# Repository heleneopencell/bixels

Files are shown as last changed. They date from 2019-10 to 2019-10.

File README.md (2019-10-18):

# bixels
 
This document will show you how to visualize fluorescent proteins with a simple DIY transilluminator / plate reader. Fluorescent proteins are widely used in biology as a research aid. In standard bio-labs you would use a transilluminator or platereader to visualize them which are wildly expensive. We will make a simple and very low-cost version of this which can be also used as a 8x8 biodisplay or as a STEAM education kit to get kids excited about biotechnology.  

[More info](https://www.bixels.io/tutorials)

### 1)[Electronic parts](https://github.com/heleneopencell/bixels#1electronic-parts)
### 2)[Cardboard box](https://github.com/heleneopencell/bixels#2cardboard-box-1)
### 3)[Assembly](https://github.com/heleneopencell/bixels#3assembly-1)
### 4)[Software](https://github.com/heleneopencell/bixels#4software-1)
### 5)[GFP - Green fluorescent proteins](https://github.com/heleneopencell/bixels#5gfp---green-fluorescent-proteins-1)
### 6)[Run an experiment](https://github.com/heleneopencell/bixels#6run-an-experiment-1)
### 7)[Timelapse with webcam](https://github.com/heleneopencell/bixels#7timelapse-with-webcam-1)
### 8)[Design Ideas](https://github.com/heleneopencell/bixels#8design-ideas-1)
### 9)[Material list](https://github.com/heleneopencell/bixels#overview-materials)
  
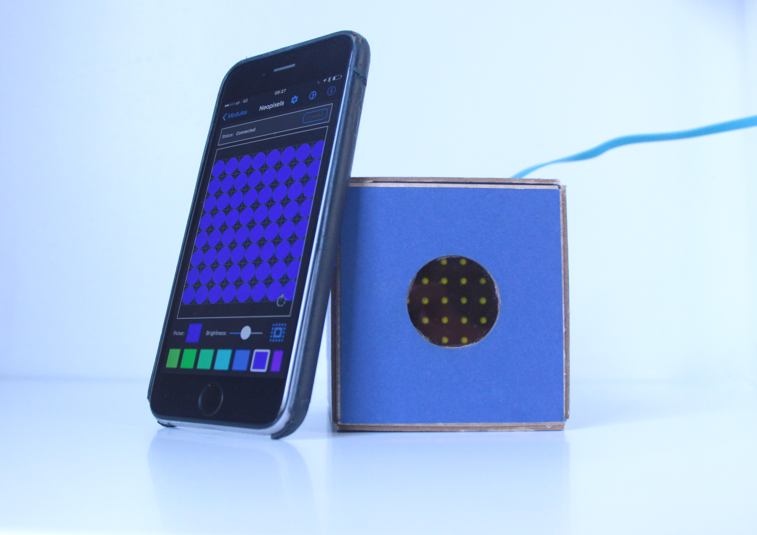
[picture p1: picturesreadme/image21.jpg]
final project
  

##### Overview
A fluorescent protein is a type of fluorescent chemical compound (fluorophore) that can re-emit light upon light excitation. If one colour of light lands on a fluorescent protein, the protein will glow with a different colour.

The story of the extraction, isolation and study of **green fluorescent protein (GFP)** is fascinating. It is also a hugely significant scientific discovery for which the 2008 Nobel Prize in Chemistry was awarded.

In this tutorial we will show you how to visualize fluorescent proteinswe. We will build a cardboard box to block out any unwanted light and use a set of optical filters. The filters allow the correct light to reach the fluorescent proteins from the LEDs and for the correct light to reach your eye from the fluorescent proteins. The diffuser simply diffuses the light evenly which is not necessary but useful if you want to use Bixels for something else than PCR tubes, for example electrophoresis gels. 

The RGB LED matrix we are using is capable of generating the required light to stimulate fluorescence in many types of fluorescent proteins.  
The filters described in this tutorial are only suitable for GFP but you can exchange them.[You can learn more here](https://www.biotek.com/assets/tech_resources/Filter%20Combinations.pdf) which filters to use for which fluorescent protein.  

The software and app we will use will allow you to control each single led and it's individual light color from your phone.  

Proteins can take up to a few hours to get expressed. We therefore added a section how to add a webcam to Bixels which takes every few minutes a picture which will create a timelapse streamed to the web. 

_____________________

### 1)Electronic parts
We will be using off-the-shelf electronics from adafruit for this project. Adafruit is super user friendly, fantastic for quick DIY projects and has a huge community to reach out for help and inspiration.
We will be using their [Adafruit Feather 32u4](https://www.adafruit.com/product/2829) board which is bluetooth enabled to control a [8x8 Neopixel LED matrix](https://www.adafruit.com/product/1487) with our phone. To power bixels we will add a [micro USB breakout](https://www.adafruit.com/product/1833). This enables you to power bixels with a power bank, your laptop or with a wall plug.

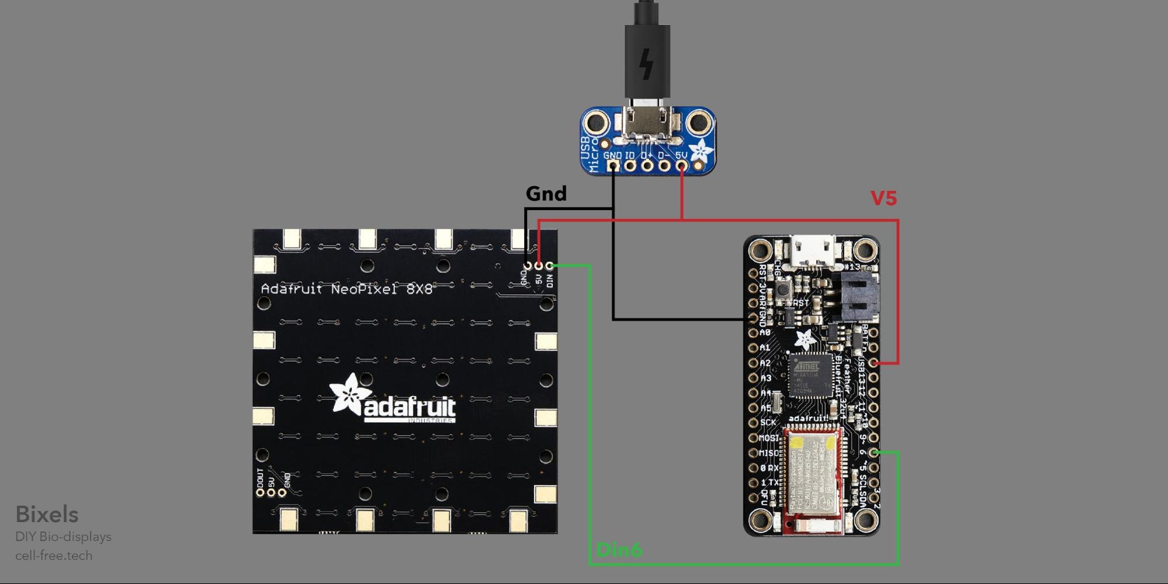
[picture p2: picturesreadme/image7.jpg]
electronic circuit


To start with we have to solder the stacking headers on the Adafruit Feather and Neopixel Matrix. I recommend using the headers rather than soldering the cables directly on the board. The headers will allows you to be much for flexible and enable you to expand your project at a later stage with useful sensors such as humdity and temperature. For the ones that are new to soldering, check out this usefull [guide to excellent soldering](https://learn.adafruit.com/adafruit-guide-excellent-soldering).

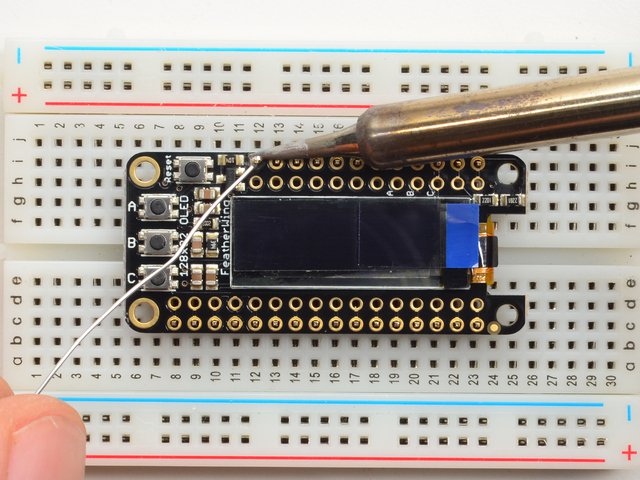
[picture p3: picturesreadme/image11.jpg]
soldering bluefruit


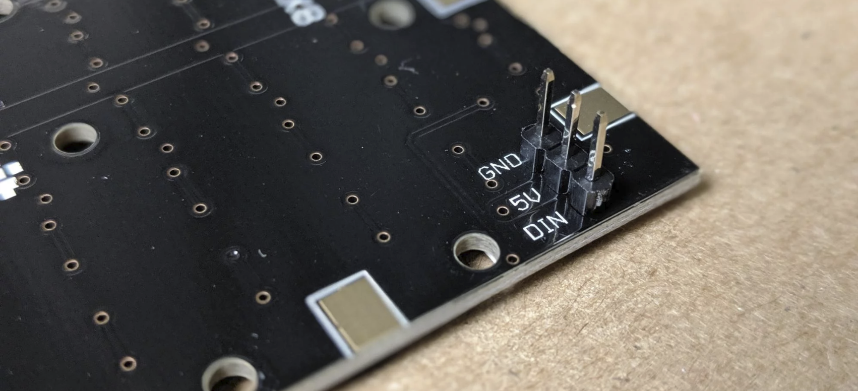
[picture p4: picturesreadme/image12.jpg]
soldering neopixel
  

To power bixels we will add a micro usb port. Take two black or brown "female to female" jumper wires and cut one end off. Connect the wire end with each other and solder it on the GND pin on the USB Micro B-Breakout board. Now take two red "female to female" jumper wire wires and cut one end off. Connect the wire end with each other and solder it on the 5V pin on the USB Micro B-Breakout board. We will use one black and one red cable to power the LEDs and one black and one red one to power the board itself.  

Note: You can also make your own wires with femaler headers but I do it the lazy way...
  
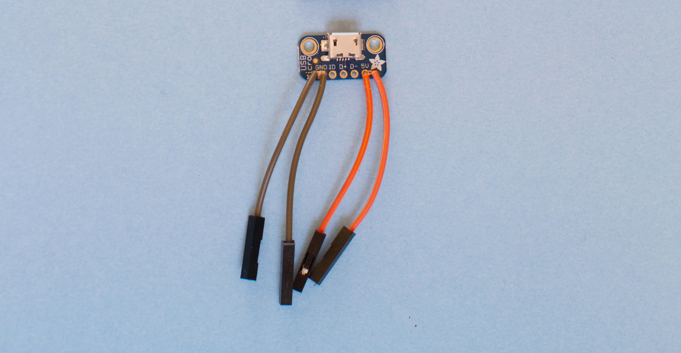
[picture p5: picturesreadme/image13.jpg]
soldering microusb


### 2)Cardboard box
Let's get started with the cover for bixels which is a simple cardboard box. I have chosen cardboard because it allows you to quickly iterate and customize the design without the need of any equipment such as a 3D printer. 

You can either lasercut your parts or print the PDF on a A3 sheet and cut it out by hand. Use a non see-through cardboard! Test it out beforehand and hold it against the light. No light should be able to get through. I use [Mountboard from Daler Rowney](https://www.amazon.co.uk/Daler-Rowney-Black-Graduate-Mountboard/dp/B00GKCF0VG/ref=sr_1_4?keywords=mount+board+black&qid=1571151582&sr=8-4) because it allows you to make neat hinges. You can also add a layer of black thin cardboard on each side if your cardboard let's any light through, use sprayglue for laminating it on top.
 
###### For the lasercut
[Download](https://github.com/heleneopencell/bixels/tree/master/lasercut) the file here. The yellow lines are for engraving the cardboard to easier fold it. The red lines are cuts. We suggest to test your two settings in a small corner beforehand.  
 
###### For cutting it by hand
[Download](https://github.com/heleneopencell/bixels/tree/master/printfiles) the files here. Print it on an A3 paper and mount it on a thicker cardboard. You don’t want anything moving. I suggest to use (removable) spray-mount for it. For the PCR matrix and it is best to use a lasercutter but it is possible to cut it by hand - a holepuncher is useful. (Just a bit fiddly)  

Note: We have made two designs for the filterbox:  

**Smaller round cut-out:** The benefit here is that less natural light gets in the box which improves the performance. This is particular useful if are planning to use it with a camera. Which I will explain in more detail in [chapter 4](chapter 4).  
**Larger cut-out:** This works better if you want to turn it into a bio-display. You can do fun things such as building your own bio-gameboy with it. Downside is that it works best in the dark because it lets more natural light in. You can also improve this by using 2 blue flights on top of each other.
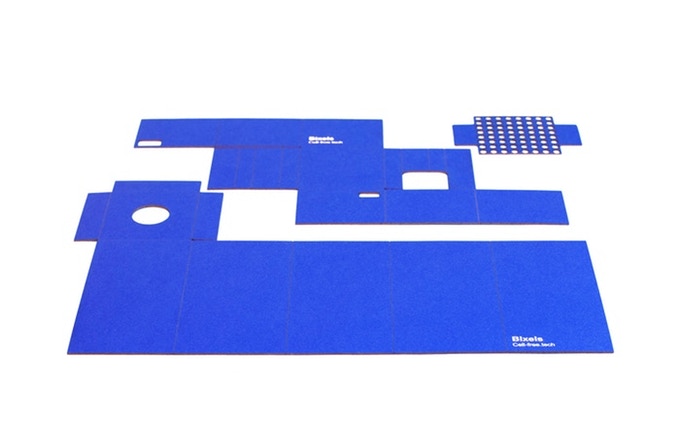
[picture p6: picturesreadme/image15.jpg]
lasercut box
  
  
### 3)Assembly
 
###### Folding the boxes
Bixels is made of 3 parts. The main box for the electronics, the filterbox to turn it into a transilluminator and our PCR matrix to hold your PCR strips in place.

First we have to mount the USB breakout board on the main box with the two M2 screws and nuts. Now let's **fold the main box** for the electronics: The inner box will be used as a platform for your led-display.  
  
fold mainbox (https://vimeo.com/259026890)

Now let’s **fold the filter box**: Glue the orange filter from on top of the cut-out. We have made two designs for this:  

**Smaller round cut-out:** The benefit here is that less natural light gets in the box which improves the performance. This is particular useful if are planning to use it with a camera. Which I will explain in more detail in [chapter 4](chapter 4).  

**Larger cut-out:** This works better if you want to turn it into a bio-display. You can do fun things such as building your own bio-gameboy with it. Downside is that it works best in the dark because it lets more natural light in. You can also improve this by using 2 blue flights on top of each other.  

fold filterbox (https://vimeo.com/259029617)

Let's **fold the PCR matrix:**  
The PCR matrix is designed to fit with PCR strips which will place each PCR tube right on top of an LED. Fill the matrix when you are ready to make your experiment to ensure they are sterile.
It is a simple matrix which can be connected without the use of any glue.  

pcr matrix (https://vimeo.com/259033478)  

Next let's connect all electronics. Connect one of the **red wires** from the micro usb breakout board to the **5V pin** on the Neopixel matrix and one red wire to the **USB pin** on Bluefruit feather board.
Now connect one of the **black wires** from the micro usb breakout board to the **GND pin** on the Neopixel matrix and one black wire to the **GND pin** on Bluefruit feather board. Next grab one of the female/female **jumper wires** and connect the **DIN pin** on the Neopixel matrix with **Pin6** on the Bluefruit feather board. Hide carefully the board in the little compartment and place the LED matrix on top. Connect the usb cable and we are ready to go.
  
assembly (https://vimeo.com/259130358)  

### 4)Software  

###### Arduino set-up for Adafruit Feather 32u4 
If you haven’t done it already, download the newest [Arduino IDE version](https://www.arduino.cc/en/main/software). Next we have to set up our Bluefruit Feather Board for Arduino as described [here](https://learn.adafruit.com/adafruit-feather-32u4-bluefruit-le/setup) and install the board with the Board Manager and install the adafruit driver as described [here](https://learn.adafruit.com/adafruit-feather-32u4-bluefruit-le/using-with-arduino-ide).  

###### Uploading Arduino sketch 
Before uploading our sketch you need to install the BLE library as described [here](https://learn.adafruit.com/adafruit-feather-32u4-bluefruit-le/installing-ble-library). 
Now download the [bixel.zip](/bixel.zip), extract or unpack it and open the file bixel.ino which is inside the folder.

It’s time to upload your code onto your device. Connect the USB from your bixel to your computer and choose the correct port inside your Arduino window. Now click upload and wait till it got successfully uploaded. It should look something like this.

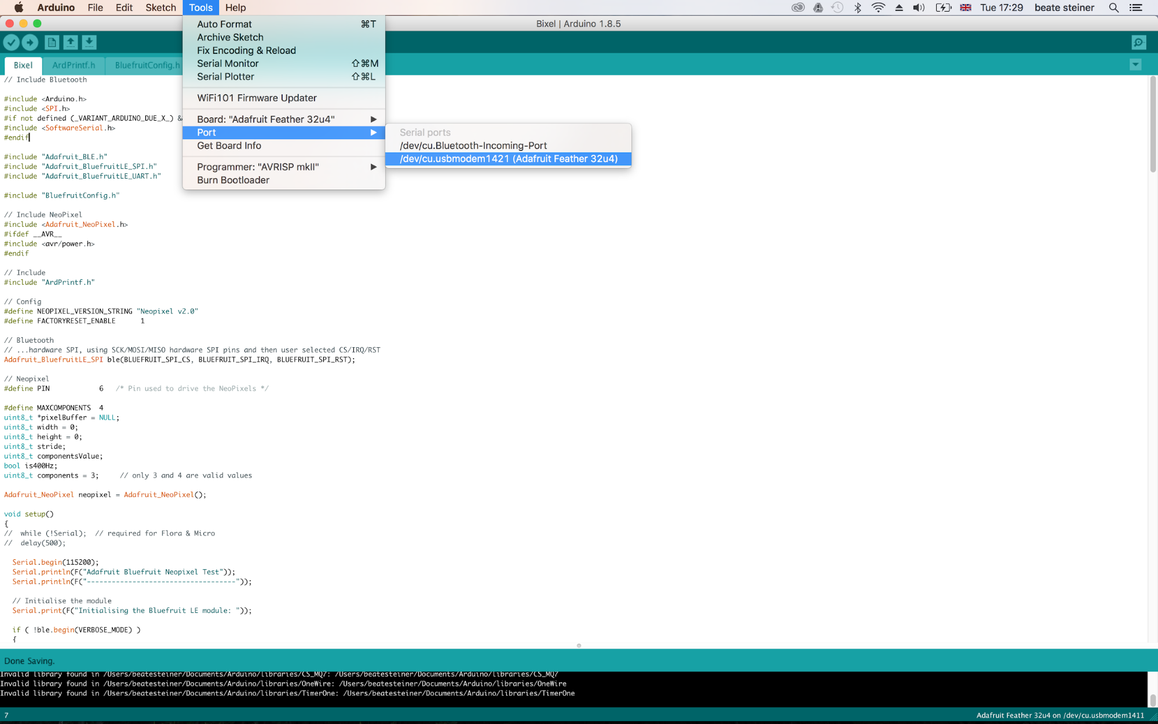
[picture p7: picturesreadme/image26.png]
choose port
  
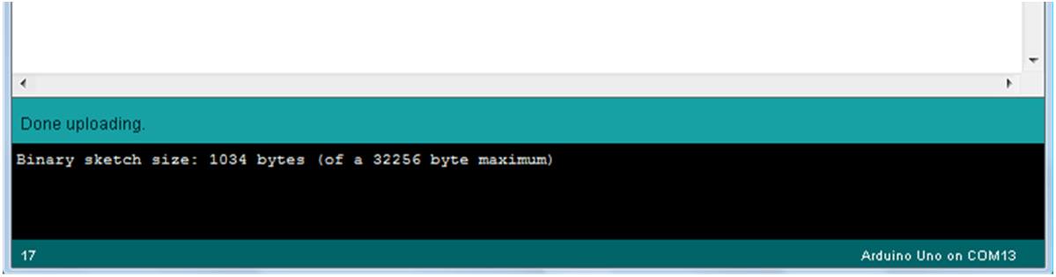
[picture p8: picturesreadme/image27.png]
upload
  
  
###### App to control the LED's
Now let’s get started with controlling the LEDs. First download the Adafruit Bluefruit LE Connect App on your phone. The app is available for [iOS](https://apps.apple.com/gb/app/adafruit-bluefruit-le-connect/id830125974) and [Android](https://play.google.com/store/apps/details?id=com.adafruit.bluefruit.le.connect&hl=en_GB).
 
Open the app and connect to your device Adafruit Bluefruit LE.
Choose the NeoPixel icon in the bottom line and press OK when it gives you a notice.
Next we have to choose the correct matrix layout. Click the settings button at the top, next to the word ‘NeoPixel’ and choose ‘8x8’.
Press ‘Connect’ and your LED’s should turn on. Now you are ready to control your individual LEDs. 

assembly (https://vimeo.com/259016118)  

### 5)GFP - Green fluorescent proteins
We need a fluorescent protein to be able to test if our transilluminator is working! So how do we make them?

In most cases we talk and share how to programme with 0's and 1's on this platform but here we would like to share how to programme with DNA, with C G T and A's.  
At the cellular level organisms are complex. A key process is the creation of proteins based on the specific instructions contained in the base pairings of deoxyribonucleic acid (DNA). Base-pairs are composed of either cytosine (C) and guanine (G) or tyrosine (T) and adenine (A). These base pair instructions can be long, the genome of a human is ~ 3 billion base pairs (3gbp), the genome of wheat is even longer at 10 gbp. The length of DNA which encodes green fluorescent protein (a single protein, and the topic of this tutorial) is about 700 bp.  

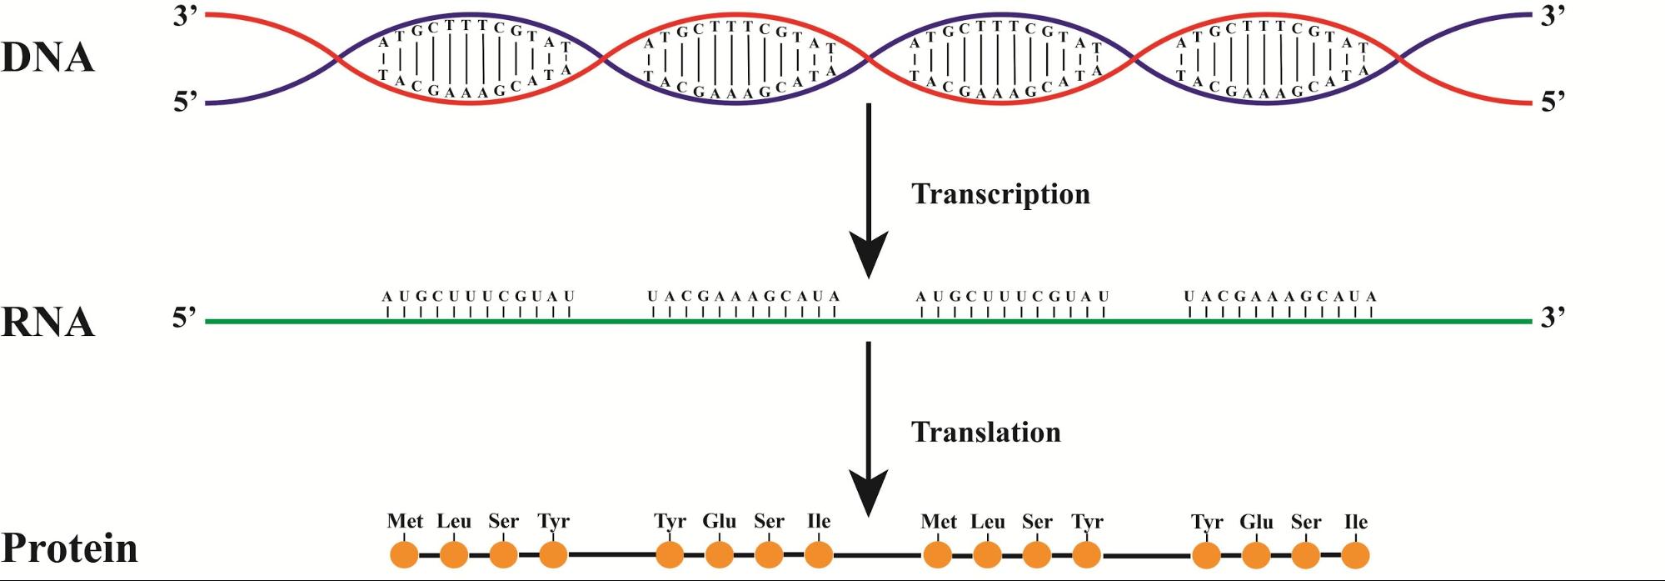
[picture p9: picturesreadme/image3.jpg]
  

A selection of DNA is transcribed when a type of protein called RNA polymerase attaches to a circuit element called a promoter (initiator of transcription), this creates a piece of RNA of length determined by the location of a terminator (stops transcription). This piece of RNA contains a ribosome-binding site to which an organelle called a ribosome adheres and begins the process of translation, where amino acid sequences are joined to form proteins. 

A piece of **DNA gives these instructions** through encoding specific operations:
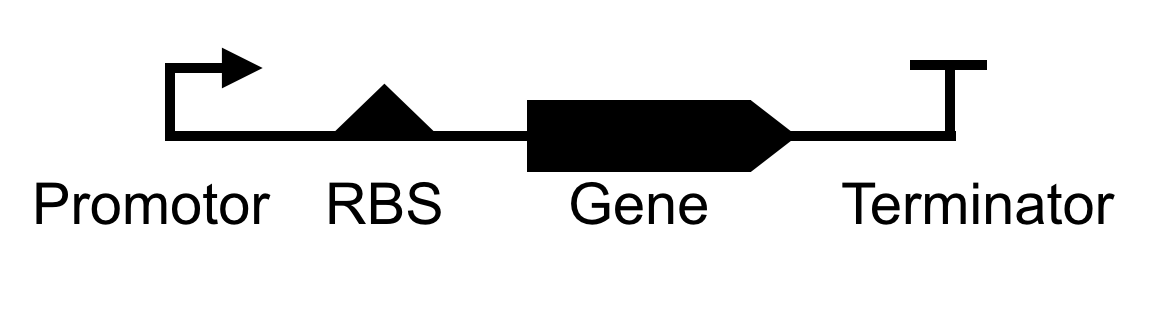
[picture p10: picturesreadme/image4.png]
  

* Promoter -  Facilitates RNA polymerase binding to initiate transcription
* Ribosome-binding site (RBS) - Initiation site for translation
* Gene - The part of the DNA code that is converted to the protein of interest
* Terminator - Halts transcription

###### How to Engineer Biology

Synthetic biology is an interdisciplinary branch of biology and engineering. It establishes the tools and techniques to build artificial biological systems for various applications. Some of the best materials to work with in this field are the simplest and most common - like DNA.

In order to understand DNA you can use a visualiser and a great service to use for this is [Benchling](https://www.benchling.com/). To get even more hands on and do it yourself you can review two sites that have everything you could ever need in terms of DNA parts. The first is Addgene, a non-profit set up with the goal of providing a facility for maintaining and storing DNA parts. They have a [dedicated site about fluorescent proteins](https://www.addgene.org/fluorescent-proteins/).  It is roughly £60 for an individual part. Secondly you could go to the [IGEM registry](http://parts.igem.org/Protein_coding_sequences/Reporters#Fluorescent_proteins) where a whole range of parts or “biobricks” are stored and can be requested (although you may need to be part of an IGEM team).

For Bixels we want to produce green fluorescent proteins, these  will glow with a different colour when one colour of light hits them. A wide range of coloured proteins (fluorophores) can be produced from DNA. This allows you to get creative with your combinations.   
  
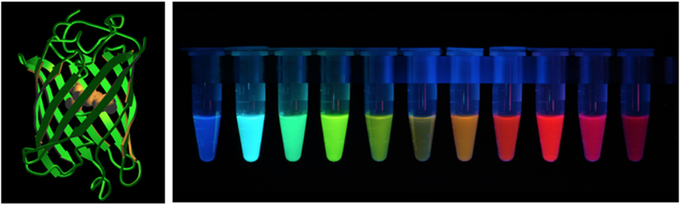
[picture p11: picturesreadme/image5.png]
different colors
  

Note: Bear in mind that different coloured proteins need to get excited with a different colour of light, which means you also have to adapt your filters. [Here](https://www.biotek.com/assets/tech_resources/11596/table1.jpg) a useful document about the different excitation wavelenghts for different proteins.
But first let's find out how to even make proteins. We will outline two ways here:

1) **By bacteria transformation**
This involves inserting a plasma into a chassi, for example E.Coli (bacteria) which will express proteins based on the plasmid incerted.
If you are new to genetic engineering we highly recommend you to get the [Zero to genetic engineering hero book](https://amino.bio/products/learn-genetic-engineering-the-genetic-engineering-hero-book) from Amino Labs. It will make teach you every step needed to make your own transformations. With the book you can get kits that will provide you with all materials needed to make your own fluorescent proteins. I recommend the [RGB kit](https://amino.bio/collections/everything/products/rgb-kit-activate-cells-with-light)!

2) **By using Cell-Free systems**
Which allows you to use and work with outside of the research lab. This involves removing the transcription and translation machinery from a cell. It allows you to make proteins without having to grow or work with live cells. Since Cell-Free expression liberates you from the requirements of a bio-lab you can begin to experiment to make your projects more tangible. You can get your cell-free kit to make your own fluorescent proteins at [minipcr.com](https://www.minipcr.com/product/biobits-central-dogma/).

### 6)[Run an experiment]()
Let's make your proteins shine. 

I love that the colors of the app are similar to different protein you can express. In our case we will excite a green fluorescent protein with blue light.
So let's turn your bixel into a transilluminator. The kit includes 3 filters. An amber filter, blue filter and and a diffuser.
We already mounted our amber filter into our filter box. To turn the main box into a transilluminator, layer the blue filter and diffuser on top of the LED matrix and place your PCR matrix (with GFP in 1 or more tubes) on top. Slide the filter box on top of the main box and turn the LEDs to blue. You can either excite single tubes or excite all in once.  

assembly (https://vimeo.com/236662582)  

If you look now through the orange filter you will only see your fluorescent proteins glow! I love to use either my phone to capture it or for timelapses a simple web-cam. Below a protocol ‘How to build a timelapse with a web-cam’.  

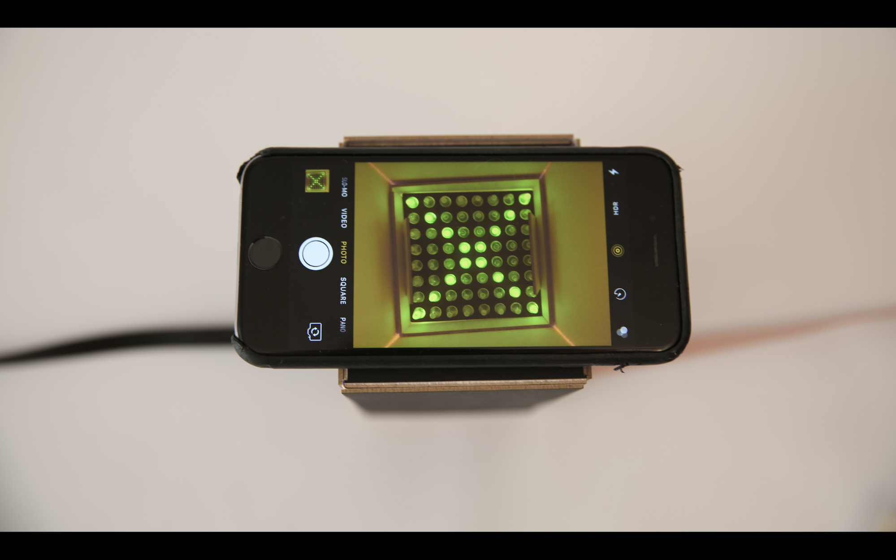
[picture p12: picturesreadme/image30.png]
transilluminator
  

### 7)Timelapse with webcam
I like to use electronics and programming not only to be creative, it allows me to be lazy.
My colleague Tom wrote a tutorial how to make a cheap timelapse and webstream with a Raspberry Pi and a webcam.
The design fits great with the bixels project. [Follow the steps here.](http://designbio.co.uk/blog/raspi-timelapse)

### 8)Design Ideas
Now it's time to get creative. We have used bixels for some fun applications so far:

**As an educational tool to teach biotechnology to non scientists**  
educational tool (https://vimeo.com/212755100)  

**Making a gameboy which has a biopixel display**  
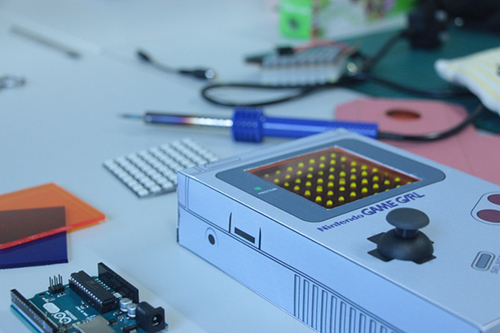
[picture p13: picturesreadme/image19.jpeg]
  

**Playing tetris with fluorescent proteins**  
  

**Test your biology experiment**  
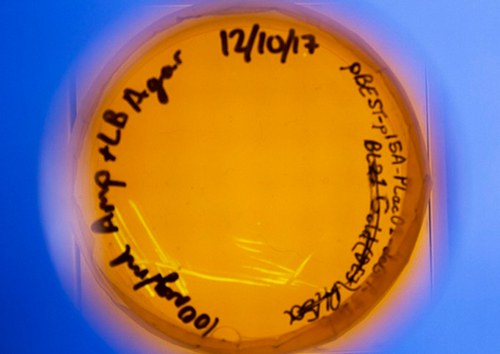
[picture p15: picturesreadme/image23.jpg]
lab
  

If you have any ideas you want to share please drop me a line at helene.steiner@rca.ac.uk

### Overview Materials  

| Electronic Parts  | Supplier EU  | Supplier US  |
|-------------------|--------------|--------------|
| 1x Neopixel Matrix |[RS Components](https://uk.rs-online.com/web/p/led-evaluation-kits/1245498/) | [Adafruit](https://www.adafruit.com/product/1487) |
| 1x Adafruit Feather 32u4 | [RS Component](http://tiny.cc/xpbmez) | [Adafruit](https://www.adafruit.com/product/2829) |
| 1x USB Micro B-Breakout   | [Amazon](http://tiny.cc/k0bmez) | [Adafruit](https://www.adafruit.com/product/1833) |
| 1x Jumper wire female/female | [RS Components](https://uk.rs-online.com/web/p/breadboard-jumper-wire-kits/7916450/) | [Adafruit](https://www.adafruit.com/product/1951)|
| 1x Micro USB Cable | [RS Components](https://uk.rs-online.com/web/p/usb-cables/8762403/) | [Adafruit](https://www.adafruit.com/product/1995)|

_____________________
  
| Filters | Supplier EU | Supplier US  |
|-------------------|--------------|--------------|
| 1x Diffuser Paper 72mm x 72mm |[Amazon](http://tiny.cc/7ecmez) | [Amazon](https://www.adafruit.com/product/1487) |
| 1x Translucent Amber Filter 72mm x 72mm | [Plastic People](https://www.theplasticpeople.co.uk/coloured-acrylic-perspex/) | [Acrylite](https://www.mcmaster.com/85635k461) |
| 1x Translucent Blue Filter 72mm x 72mm | [Plastic People](https://www.theplasticpeople.co.uk/coloured-acrylic-perspex/) | [Acrylite](https://www.mcmaster.com/85635k461) |
_____________________
  
| Cover / Box | Supplier EU  | Supplier US  |
|-------------------|--------------|--------------|
| 1x Cardboard |[Amazon](http://tiny.cc/vwdmez) | [Amazon](http://tiny.cc/xzdmez) |
| 1x Double sided tape| [Amazon](http://tiny.cc/fqdmez) | [Amazon](http://tiny.cc/jtdmez) |
| 1x Superglue | [Amazon](http://tiny.cc/9odmez) | [Amazon](http://tiny.cc/nndmez)|
| 2x M2 Hex Nut | [RS Compnent](https://uk.rs-online.com/web/p/hex-nuts/0560271/) | [Amazon](http://tiny.cc/nndmez)|
| 2x M2 Hex Screw | [RS Compnent](https://uk.rs-online.com/web/p/connector-screws-nuts/1665038/) | [Amazon](http://tiny.cc/nndmez)|

_____________________
  
| Equipment | Supplier EU  | Supplier US  |
|-------------------|--------------|--------------|
| Lasercutter or | local makerlab | local makerlab |
| Cutter | [Amazon](https://www.amazon.co.uk/Silverline-789397-Zinc-Alloy-Snap-Off-Utility/dp/B003TNYHHW/ref=sr_1_5?keywords=cutter&qid=1571219430&sr=8-5) | [Amazon](http://tiny.cc/6gdmez) |
| Mobile phone | Android or | iOS |
_____________________
  
| Software | Supplier EU  | Supplier US  |
|-------------------|--------------|--------------|
| Arduino |[Windows](https://www.arduino.cc/en/guide/windows) | [OS X](https://www.arduino.cc/en/guide/macOSX) |
| Bluefruit LE Connect | [Android](https://play.google.com/store/apps/details?id=com.adafruit.bluefruit.le.connect&hl=en_GB) | [iOS](https://apps.apple.com/gb/app/adafruit-bluefruit-le-connect/id830125974) |
_____________________
  
| Biological Parts | Supplier EU  | Supplier US  |
|-------------------|--------------|--------------|
| Fluorescent Protein Kit (RGB) |[Amino Labs](https://amino.bio/collections/everything/products/rgb-kit-activate-cells-with-light) | [Amino Labs](https://amino.bio/collections/everything/products/rgb-kit-activate-cells-with-light) |
| Mini Lab: BioExplorer™  | [Amino Labs](https://amino.bio/collections/everything/products/bioproduction-lab?variant=40528228676) | [Amino Labs](https://amino.bio/collections/everything/products/bioproduction-lab?variant=40528228676) |
| Cell-Free  | [Mini PCR](https://www.minipcr.com/product/biobits-central-dogma/) | [Mini PCR](https://www.minipcr.com/product/biobits-central-dogma/)|
_____________________
_____________________

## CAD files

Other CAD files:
lasercut/pcrmatrix.dxf

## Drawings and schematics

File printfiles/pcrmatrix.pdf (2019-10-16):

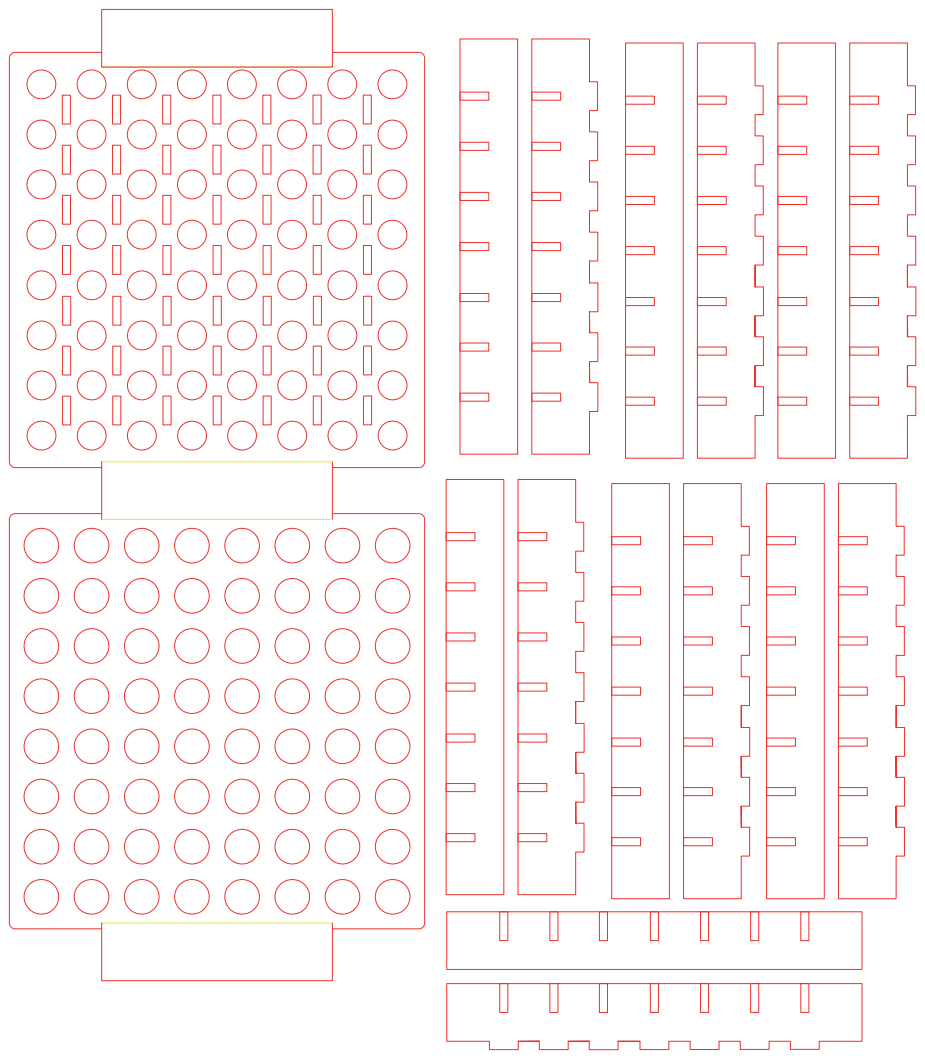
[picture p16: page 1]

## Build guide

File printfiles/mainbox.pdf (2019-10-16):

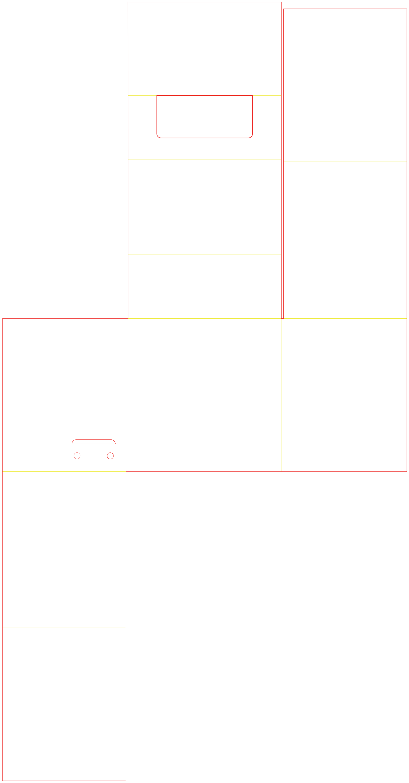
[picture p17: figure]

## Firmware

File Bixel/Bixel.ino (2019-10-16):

// Include Bluetooth

#include <Arduino.h>
#include <SPI.h>
#if not defined (_VARIANT_ARDUINO_DUE_X_) && not defined (_VARIANT_ARDUINO_ZERO_)
#include <SoftwareSerial.h>
#endif

#include "Adafruit_BLE.h"
#include "Adafruit_BluefruitLE_SPI.h"
#include "Adafruit_BluefruitLE_UART.h"

#include "BluefruitConfig.h"

// Include NeoPixel
#include <Adafruit_NeoPixel.h>
#ifdef __AVR__
#include <avr/power.h>
#endif

// Include
#include "ArdPrintf.h"

// Config
#define NEOPIXEL_VERSION_STRING "Neopixel v2.0"
#define FACTORYRESET_ENABLE      1

// Bluetooth
// ...hardware SPI, using SCK/MOSI/MISO hardware SPI pins and then user selected CS/IRQ/RST
Adafruit_BluefruitLE_SPI ble(BLUEFRUIT_SPI_CS, BLUEFRUIT_SPI_IRQ, BLUEFRUIT_SPI_RST);

// Neopixel
#define PIN            6   /* Pin used to drive the NeoPixels */

#define MAXCOMPONENTS  4
uint8_t *pixelBuffer = NULL;
uint8_t width = 0;
uint8_t height = 0;
uint8_t stride;
uint8_t componentsValue;
bool is400Hz;
uint8_t components = 3;     // only 3 and 4 are valid values

Adafruit_NeoPixel neopixel = Adafruit_NeoPixel();

void setup()
{
//  while (!Serial);  // required for Flora & Micro
//  delay(500);

  Serial.begin(115200);
  Serial.println(F("Adafruit Bluefruit Neopixel Test"));
  Serial.println(F("------------------------------------"));

  // Initialise the module
  Serial.print(F("Initialising the Bluefruit LE module: "));

  if ( !ble.begin(VERBOSE_MODE) )
  {
    error(F("Couldn't find Bluefruit, make sure it's in CoMmanD mode & check wiring?"));
  }
  Serial.println( F("OK!") );

  // Factory Reset
  if ( FACTORYRESET_ENABLE )
  {
    /* Perform a factory reset to make sure everything is in a known state */
    Serial.println(F("Performing a factory reset: "));
    if ( ! ble.factoryReset() ) {
      error(F("Couldn't factory reset"));
    }
  }

  /* Disable command echo from Bluefruit */
  ble.echo(false);

  Serial.println("Requesting Bluefruit info:");
  /* Print Bluefruit information */
  ble.info();

  /* Wait for a connection before starting the test */
  Serial.println("Waiting for a BLE connection to continue ...");

  ble.verbose(false);  // debug info is a little annoying after this point!

  while ( !ble.isConnected() )
  {
    delay(10);
  }
  
  // Wait for the connection to complete
  delay(1000);

  Serial.println(F("CONNECTED!"));
  Serial.println(F("**********"));

  // Set module to DATA mode
  Serial.println( F("Switching to DATA mode!") );
  ble.setMode(BLUEFRUIT_MODE_DATA);

  Serial.println(F("******************************"));

  // Neopixels
  neopixel.begin();
}

void loop()
{
  // Echo received data
  while ( ble.isConnected() )
  {
    int command = ble.read();

    switch (command) {
      case 'V': {   // Get Version
          commandVersion();
          break;
        }
  
      case 'S': {   // Setup dimensions, components, stride...
          commandSetup();
          break;
       }

      case 'C': {   // Clear with color
          commandClearColor();
          break;
      }

      case 'B': {   // Set Brightness
          commandSetBrightness();
          break;
      }
            
      case 'P': {   // Set Pixel
          commandSetPixel();
          break;
      }
  
      case 'I': {   // Receive new image
          commandImage();
          break;
       }

    }
  }
}

void swapBuffers()
{
  uint8_t *base_addr = pixelBuffer;
  int pixelIndex = 0;
  for (int j = 0; j < height; j++)
  {
    for (int i = 0; i < width; i++) {
      if (components == 3) {
        neopixel.setPixelColor(pixelIndex, neopixel.Color(*base_addr, *(base_addr+1), *(base_addr+2) ));
      }
      else {
        neopixel.setPixelColor(pixelIndex, neopixel.Color(*base_addr, *(base_addr+1), *(base_addr+2), *(base_addr+3) ));
      }
      base_addr+=components;
      pixelIndex++;
    }
    pixelIndex += stride - width;   // move pixelIndex to the next row (take into account the stride)
  }
  neopixel.show();

}

void commandVersion() {
  Serial.println(F("Command: Version check"));
  sendResponse(NEOPIXEL_VERSION_STRING);
}

void commandSetup() {
  Serial.println(F("Command: Setup"));

  width = ble.read();
  height = ble.read();
  stride = ble.read();
  componentsValue = ble.read();
  is400Hz = ble.read();
  
  neoPixelType pixelType;
  pixelType = componentsValue + (is400Hz ? NEO_KHZ400 : NEO_KHZ800);

  components = (componentsValue == NEO_RGB || componentsValue == NEO_RBG || componentsValue == NEO_GRB || componentsValue == NEO_GBR || componentsValue == NEO_BRG || componentsValue == NEO_BGR) ? 3:4;
  
  ardprintf("\tsize: %dx%d", width, height);
  ardprintf("\tstride: %d", stride);
  ardprintf("\tpixelType %d", pixelType );
  ardprintf("\tcomponents: %d", components);

  if (pixelBuffer != NULL) {
      delete[] pixelBuffer;
  }

  uint32_t size = width*height;
  pixelBuffer = new uint8_t[size*components];
  neopixel.updateLength(size);
  neopixel.updateType(pixelType);
  neopixel.setPin(PIN);

  // Done
  sendResponse("OK");
}

void commandSetBrightness() {
  Serial.println(F("Command: SetBrightness"));

   // Read value
  uint8_t brightness = ble.read();

  // Set brightness
  neopixel.setBrightness(brightness);

  // Refresh pixels
  swapBuffers();

  // Done
  sendResponse("OK");
}

void commandClearColor() {
  Serial.println(F("Command: ClearColor"));

  // Read color
  uint8_t color[MAXCOMPONENTS];
  for (int j = 0; j < components;) {
    if (ble.available()) {
      color[j] = ble.read();
      j++;
    }
  }

  // Set all leds to color
  int size = width * height;
  uint8_t *base_addr = pixelBuffer;
  for (int i = 0; i < size; i++) {
    for (int j = 0; j < components; j++) {
      *base_addr = color[j];
      base_addr++;
    }
  }

  // Swap buffers
  Serial.println(F("ClearColor completed"));
  swapBuffers();

  if (components == 3) {
    ardprintf("\tclear (%d, %d, %d)", color[0], color[1], color[2] );
  }
  else {    
    ardprintf("\tclear (%d, %d, %d, %d)", color[0], color[1], color[2], color[3] );
  }
  
  // Done
  sendResponse("OK");
}

void commandSetPixel() {
  Serial.println(F("Command: SetPixel"));

  // Read position
  uint8_t x = ble.read();
  uint8_t y = ble.read();

  // Read colors
  uint32_t pixelOffset = y*width+x;
  uint32_t pixelDataOffset = pixelOffset*components;
  uint8_t *base_addr = pixelBuffer+pixelDataOffset;
  for (int j = 0; j < components;) {
    if (ble.available()) {
      *base_addr = ble.read();
      base_addr++;
      j++;
    }
  }

  // Set colors
  uint32_t neopixelIndex = y*stride+x;
  uint8_t *pixelBufferPointer = pixelBuffer + pixelDataOffset;
  uint32_t color;
  if (components == 3) {
    color = neopixel.Color( *pixelBufferPointer, *(pixelBufferPointer+1), *(pixelBufferPointer+2) );
    ardprintf("\tcolor (%d, %d, %d)",*pixelBufferPointer, *(pixelBufferPointer+1), *(pixelBufferPointer+2) );
  }
  else {
    color = neopixel.Color( *pixelBufferPointer, *(pixelBufferPointer+1), *(pixelBufferPointer+2), *(pixelBufferPointer+3) );
    ardprintf("\tcolor (%d, %d, %d, %d)", *pixelBufferPointer, *(pixelBufferPointer+1), *(pixelBufferPointer+2), *(pixelBufferPointer+3) );    
  }
  neopixel.setPixelColor(neopixelIndex, color);
  neopixel.show();

  // Done
  sendResponse("OK");
}

void commandImage() {
  ardprintf("Command: Image %dx%d, %d, %d", width, height, components, stride);
  
  // Receive new pixel buffer
  int size = width * height;
  uint8_t *base_addr = pixelBuffer;
  for (int i = 0; i < size; i++) {
    for (int j = 0; j < components;) {
      if (ble.available()) {
        *base_addr = ble.read();
        base_addr++;
        j++;
      }
    }

/*
    if (components == 3) {
      uint32_t index = i*components;
      ardprintf("\tp%d (%d, %d, %d)", i, pixelBuffer[index], pixelBuffer[index+1], pixelBuffer[index+2] );
    }
    */
  }

  // Swap buffers
  Serial.println(F("Image received"));
  swapBuffers();

  // Done
  sendResponse("OK");
}

void sendResponse(char *response) {
    ardprintf("Send Response: %s", response);
    ble.write(response, strlen(response)*sizeof(char));
}

// A small helper
void error(const __FlashStringHelper*err) {
  Serial.println(err);
  while (1);
}
